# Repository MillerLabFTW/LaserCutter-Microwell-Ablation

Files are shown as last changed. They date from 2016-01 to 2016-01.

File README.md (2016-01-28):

# Laser Cutter Setup for Ablation of Microwells in PDMS

See accompanying journal article for more information: 
DOI: 10.1039/C5RA26022A 

##### A modified laser cutter platform for ablating microwells into PDMS
##### Miller Lab: Physiological Systems Engineering and Advanced Materials
##### [millerlab.rice.edu] (http://millerlab.rice.edu)
&nbsp;

MillerLab logo

We have custom modified a commercial SeeMeCNC laser cutter to selectively ablate microwell structures in PDMS. Using the modified laser cutter and our python scripts, you can print hexagonally packed arrays of microwells.

### Documentation
This git repository includes:
- STL files for 3D printing custom parts for the laser cutter
- Current Marlin firmware (modified Marlin for laser cutters courtesy of Tim Schmidt, Lansing-Maker-Network)
- Python scripts for G-code creation
- Wiring Diagram for electronics configuation (based on RAMBo electronics)
- Instructions for operating the laser cutter
- Bill of Materials

### Acknowledgements

The initial influence for using a laser cutter to ablate conical microwells comes from Roger Kamm's group at MIT:

Tu, Ting-Yuan, et al. "Rapid prototyping of concave microwells for the formation of 3D multicellular cancer aggregates for drug screening." Advanced healthcare materials 3.4 (2014): 609-616.

Tim Schmidt from the Lansing Makers Network developed the custom Marlin firmware for controlling a laser cutter.

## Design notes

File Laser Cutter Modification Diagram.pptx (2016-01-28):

## Laser Cutter Modifications

By: Jacob Albritton

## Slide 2

Z-axis linear actuator

3D Printed Vacuum hose holder

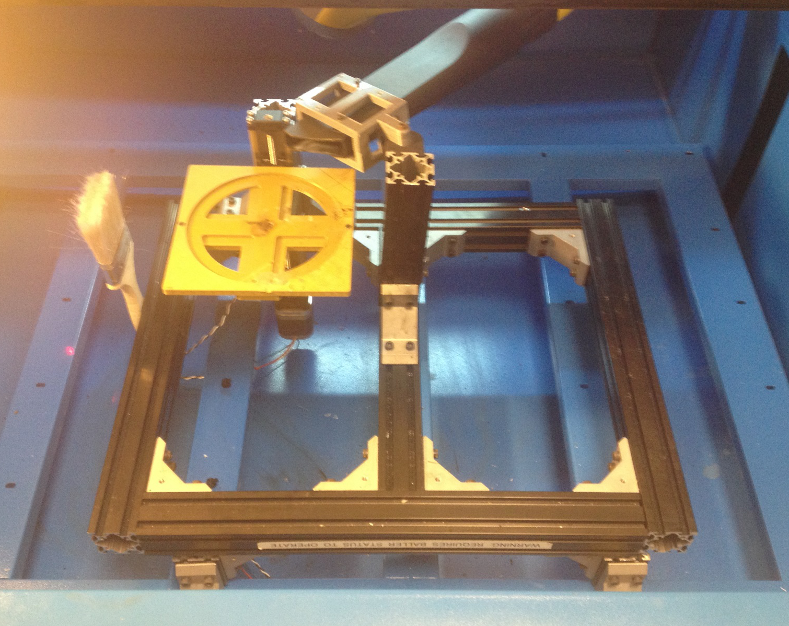
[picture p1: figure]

Laser Head Cleaning Brush

3D Printed platform

(Underneath the frame)

Z-axis motor

Frame Attachment to Laser Cutter

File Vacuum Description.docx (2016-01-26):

Updated Vacuum System

A vacuum holder has been added to the stage to secure the vacuum hose. The STL files for the vacuum hose holder parts can be found in the "STL for laser cutter" folder.

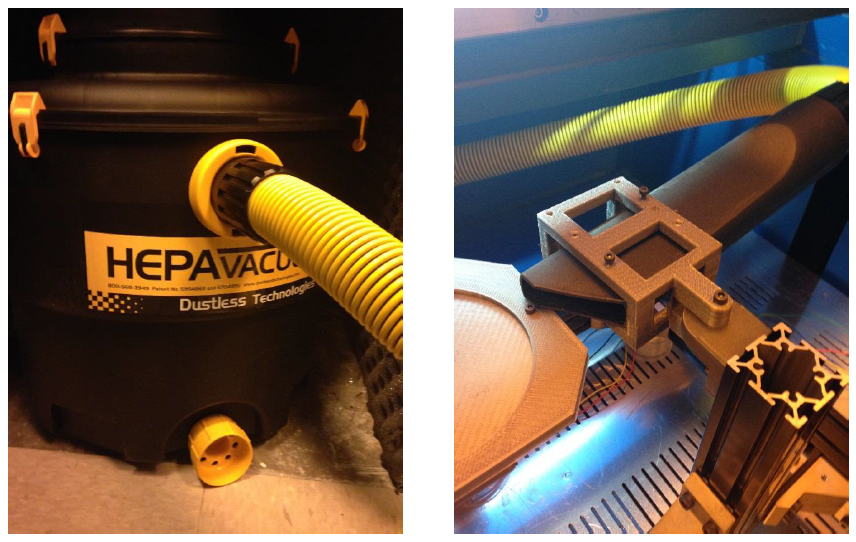
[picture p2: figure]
Machine generated alternative text: HEPAWC Dustkss т

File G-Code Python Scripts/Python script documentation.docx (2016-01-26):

Laser-ablation-GUI

This folder contains the major script for patterning rectangular arrays of microwells with the same laser parameters.

run.py

*****YOU MUST CHANGE THE FOCUS VARIABLE IN RUN.PY TO RUN PROPERLY. You can find the z-axis focus point by following the "focal point" protocol in the "Laser cutter operation" folder.

Tkinter GUI for making GCODE files for ablating PDMS with the laser cutter. The program displays a simple user interface with parameter boxes for all of the relevant parameters necessary to print.

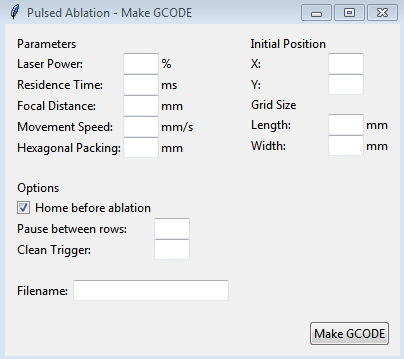
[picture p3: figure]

Pressing the Make GCODE button will create a file in a separate GCODE folder with a time and date stamp inside the filename.

NOTE: Must be run as using Python 3. Not compatible with Python 2.

Laser-ablation-functions

A few functions that can be used to create different patterns of microwells.

P-scan

Run script by running pscan.py. You can modify the config.py file to change the laser cutting parameters manually.

This program is a diagnostic tool for finding microwells of different dimensions. The program outputs a rough 3D matrix of microwell conditions based on inputs from "laserPowers", "dwellTimes" and "zValues".

The orientation parameter at the bottom will determine how the dimensions are displayed. See comments for details.

It is important to set the focus correctly. (See run.py description).

Circle-cut

Run script by running circle-cut.py. You can modify the config.py file to change the cut parameters.

Script to cut n-sided polygons with Laser Cutter toolchain. Parameters are currently optimized for cutting PDMS with our current z-axis system.

The current implementation (as of 5/2015) requires that the parameters be manually modified from the config.py file.

µWells-multishape

Run pulse.py.

Config.py file can be modified to change the parameters. Currently the simple script prints rows of alternative laser profile parameters. Each profile is the nth element of the array lists for laserPower, dwellTime, and zValue.

In theory, any number of laser profiles can be interleaved, but the program is not designed to account for printing too many shapes.

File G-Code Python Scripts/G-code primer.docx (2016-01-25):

GCODE Primer for Laser Cutter Control

General Information

Gcode is a very simple code designed to control 3D printers. We have an adapted version of a GCODE interpreter courtesy of Tim Schmidt from the Lansing Makers Network (https://github.com/lansing-makers-network/buildlog-lasercutter-marlin) that has been augmented to better control laser based machines like our laser cutter.

The flow of Gcode is fairly simple. Commands are given line by line with appropriate arguments. For example, a typical move command would look like this:

“G0 X1 Y2 Z3 F1000”

The initial command G0 specifies the function G0 to be applied. The following arguments are comprised of an initial letter to describe the type of argument, and a numerical value to quantify the argument. For example, the letters X, Y, and Z denote coordinates in the X, Y, and Z directions respectively. The numbers following X, Y, and Z show the coordinate value to move towards. The F value is a different argument, which specifies the movement speed. So 1000 quantifies how fast to move for this variable.

The Gcode RepRap wiki (http://reprap.org/wiki/G-code) gives a fairly comprehensive list of Gcode commands and appropriate descriptions. There are different Gcode interpreters including our interpreter (Marlin).

Interpreter firmware/Gcode syntax has been extensively used by the RepRap community to simplify the ability to control 3D printing movement. It is important to note though, that Gcode simply encodes for firing of electrical pulses in a predefined manner. So, even though Gcode was not designed for controlling a laser cutter, commands can be co-opted for unorthodox uses if the controller board is correctly wired to the laser cutter.

Below is a list of Gcode commands specific to our laser cutter/Marlin firmware setup with accompanying arguments and descriptions.

Important Commands for Controlling our Firmware

  - M649
    - Set Laser Fire Settings
    - Arguments
      - S
        - Laser Intensity
        - Values are 0 to 100 (float type)
        - Units are % laser power
      - L
        - Duration of laser pulse
        - Values are integers
        - Units are microseconds (μs)
      - P
        - Pulses per millimeter
        - Values are float type
        - Resolution discussed below
      - B
        - “Beam type”
        - 0 for continuous fire
        - 1 for Pulsed mode (note: specifying “P” should automatically change to B1 mode)
        - 2 for raster mode
      - D
        - Diagnostics
        - Logical 0 or 1 for whether to output diagnostics
  - M3
    - Turn laser on with current laser settings
    - Laser settings can be specified with an M3 command, but if a setting is not specified, the previously used value will be used.
  - M5
    - *****Turn laser off
  - G0
    - Move without laser on
    - Behaves identically with old marlin Gcode
  - G1
    - Move with laser on
    - Uses previously stored laser settings
    - Can take arguments from M649 to customize laser settings
  - M114
    - Obtain current coordinates
    - Enter directly to pronterface
    - Can be input while printing without disrupting the current print
  - G92
    - Set Coordinates
    - Takes X, Y, and Z arguments
  - G90
    - Set absolute coordinates
    - G0/G1 commands with X, Y, and Z will specify absolute coordinate locations
    - i.e. if you enter G0 X1 Y2 Z3 twice, the first command will move to (1,2,3) and the second command will not move (because you are already at the specified locations)
  - G91
    - Set relative coordinates
    - G0/G1 commands with X,Y, and Z will specify a relative movement direction
    - i.e. G0 X1 Y2 Z3 twice will move in a <1,2,3> vector direction twice to a final destination of (2, 4, 6) relative to the initial position
  - M84
    - Turn motors off

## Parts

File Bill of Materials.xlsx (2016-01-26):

Qty | Item | Vendor | Part No. | Cost Per Item | Total Cost | Notes
1 | CO2 Laser Cutter and Engraver With Auto Focus, Max 100W, RECI CO2 Glass Tube, Auto Focus, 48 ″ x 36″ - See more at: | Automation Technologies, Inc. |  | $8999.00 | $8999.00 | We use SeeMeCNC version that is no longer sold; this appears to be similar but may have different wiring
1 | RAMBo v1.3 Complete Kit w/ Mechanical Endstop Switches w/ Wiring | Ultimachine | UMRAMBOPAC13 | $170.00 | $170.00
1 | Kysan 1124090 Nema 17 Stepper Motor (z-motor) | Ultimachine | UMN17MTR | $14.50 | $14.50
1 | KR20 - 120mm stroke Linear motion actuator (z-axis) | THK |  | $200.00 | $200.00 | Actual price varies on Ebay
3 | Aluminum Frame | Misumi | HFSB5-4040-55 | $7.99 | $23.97
1 | Aluminum Frame | Misumi | HFSB5-4040-120 | $7.99 | $7.99
1 | Aluminum Frame | Misumi | HFSB5-4040-160 | $7.99 | $7.99
1 | Aluminum Frame | Misumi | HFSB5-4040-320 | $8.54 | $8.54
4 | Aluminum Frame | Misumi | HFSB5-4040-400 | $10.68 | $42.72
1 | Nuts for Aluminum Frames | Misumi | PACK-HNTT5-5 | $32.20 | $32.20
18 | Aluminum bracket | Misumi | HBLFUD5-C | $2.70 | $48.60
1 | paintbrush | various |  |  | $0.00
1 | Dustless Technologies 16006 16-Gallon Dustless Wet/Dry Vacuum with Hepa Filter | Amazon |  | $481.77 | $481.77
1 | Dustless Technologies 13141 Wet Dry Micro Pre Filter Bag, 2-Pack | Amazon |  | $19.95 | $19.95

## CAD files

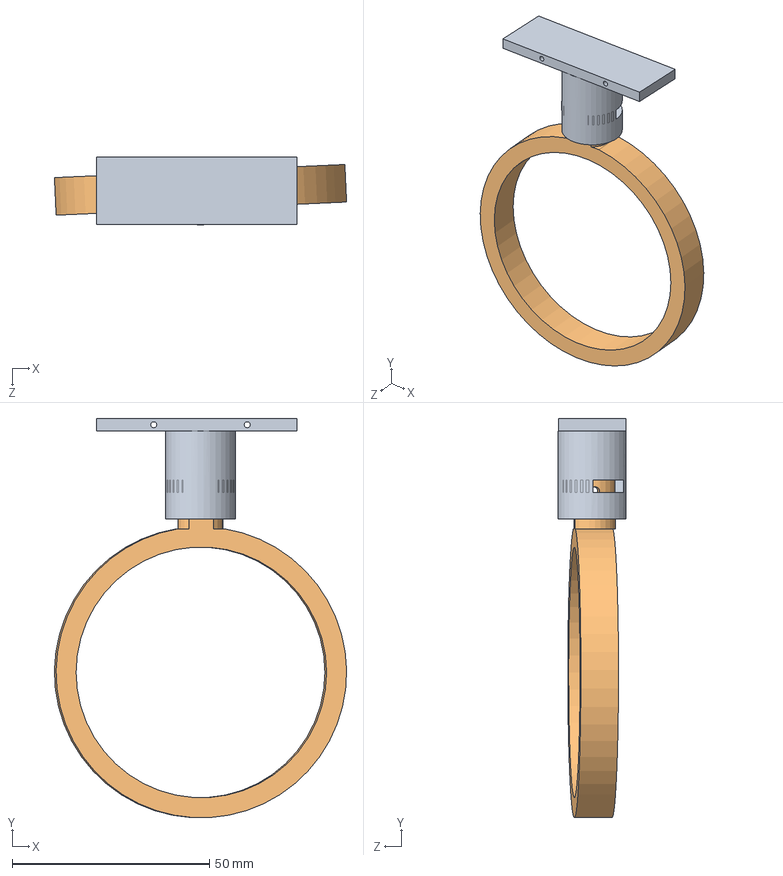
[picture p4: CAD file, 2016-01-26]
STL for laser cutter/VacuumHolder/VacuumFasten_002.SLDASM
74.0 x 101.1 x 17.1 mm
VacuumCuff
VacuumRing

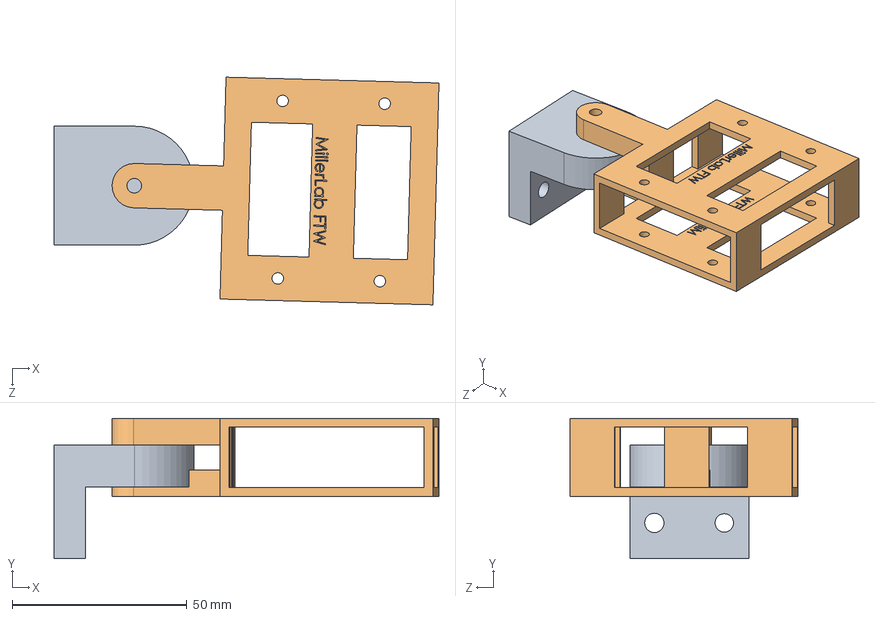
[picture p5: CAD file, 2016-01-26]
STL for laser cutter/VacuumHolder/VacuumFasten_001.SLDASM
110.2 x 40.1 x 65.1 mm
VacuumHinge
VacuumHolder

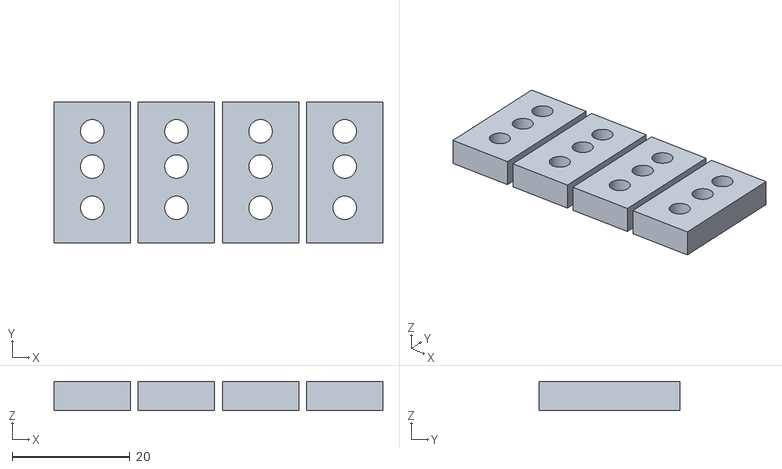
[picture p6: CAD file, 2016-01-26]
STL for laser cutter/Endstop holders/LaserCutter-Y-EndstopHolder.stl
55.9 x 24.0 x 5.00

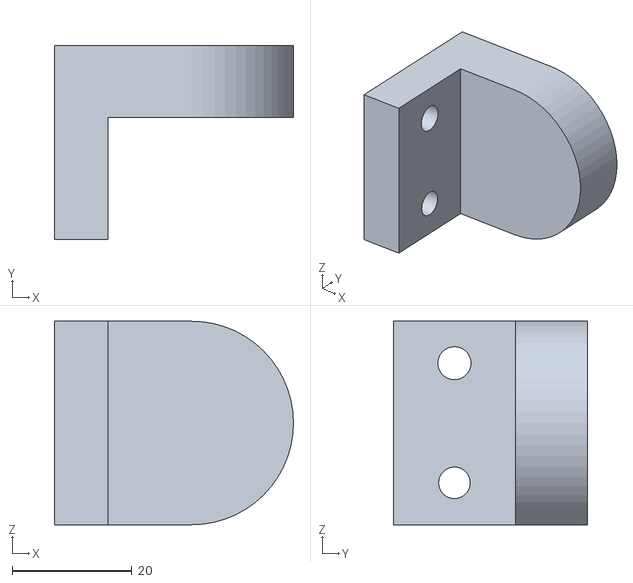
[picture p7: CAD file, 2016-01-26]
STL for laser cutter/Z-axis stage/VacuumHinge.STL
40.0 x 32.5 x 34.1

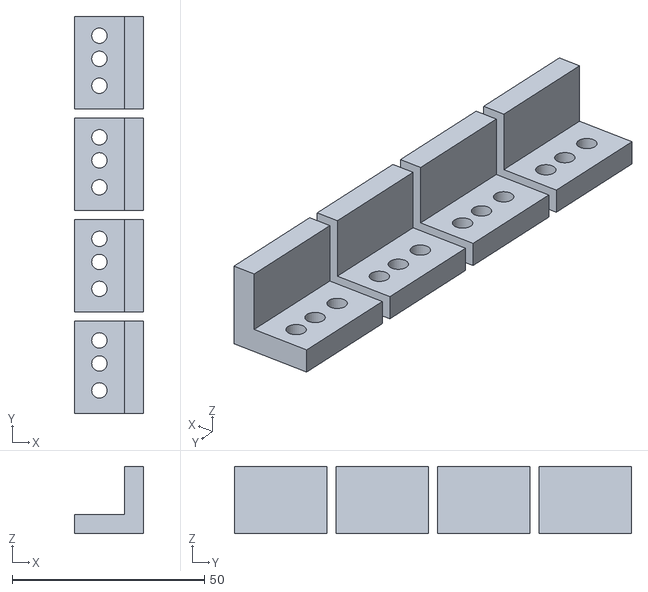
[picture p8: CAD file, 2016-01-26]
STL for laser cutter/Endstop holders/LaserCutter-X-EndstopHolder.stl
18.0 x 103.2 x 17.5

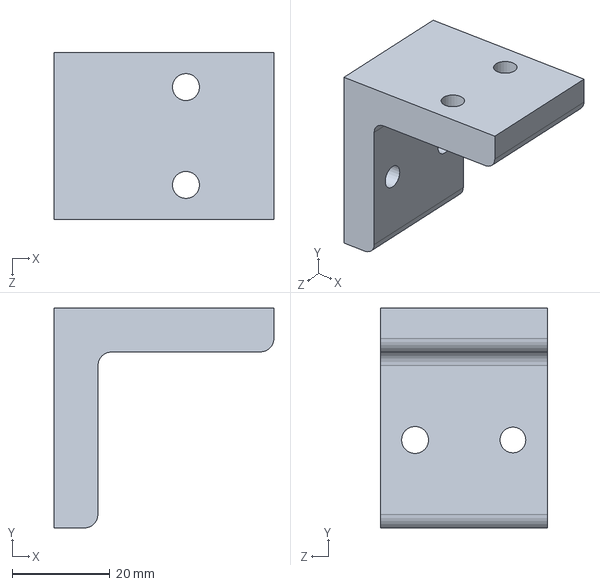
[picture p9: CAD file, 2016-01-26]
STL for laser cutter/Z-axis stage/80-20Bracket.SLDPRT
45.0 x 45.0 x 34.1 mm

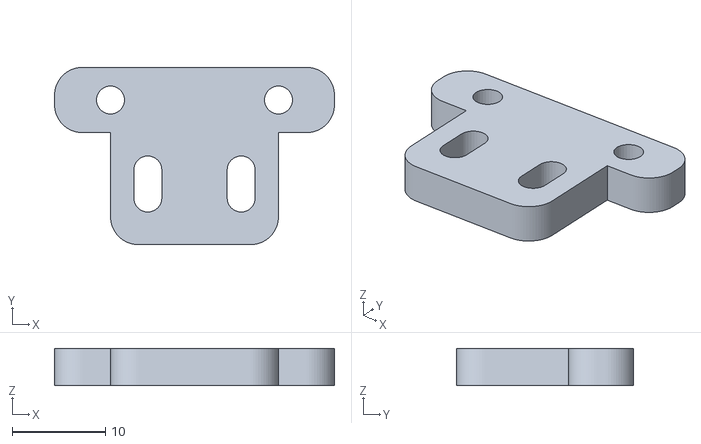
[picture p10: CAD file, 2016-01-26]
STL for laser cutter/Endstop holders/LaserCutter-Z-EndstopHolder.stl
30.0 x 19.0 x 4.00

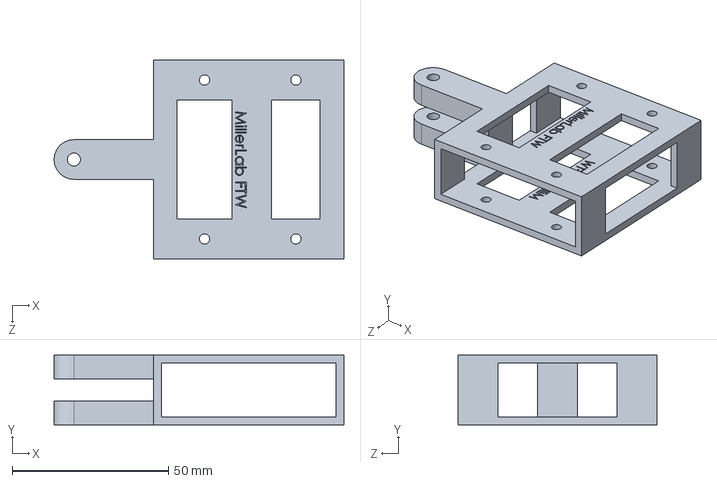
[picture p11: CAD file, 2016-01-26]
STL for laser cutter/VacuumHolder/VacuumHolder.SLDPRT
92.7 x 22.4 x 63.5 mm

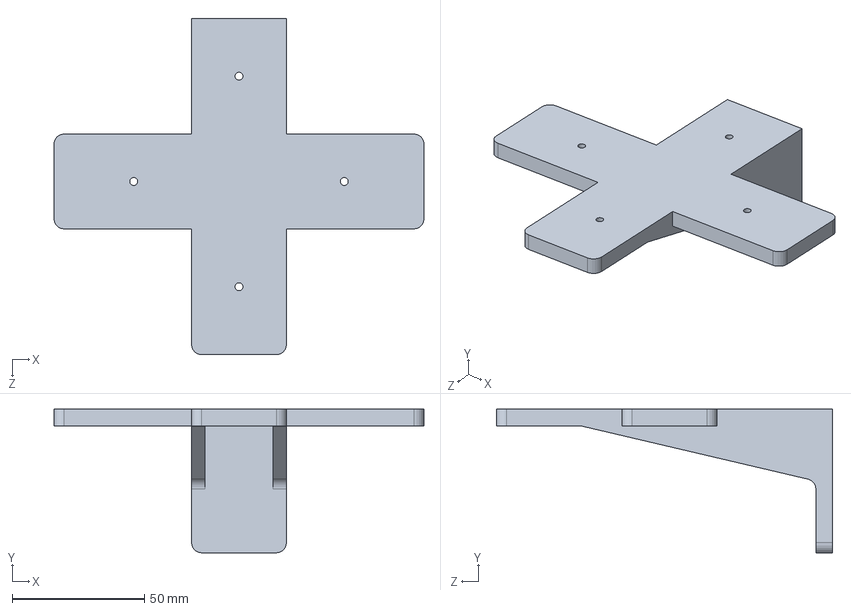
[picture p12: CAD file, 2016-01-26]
STL for laser cutter/Z-axis stage/Z-Stage_002.SLDPRT
139.7 x 54.2 x 127.0 mm

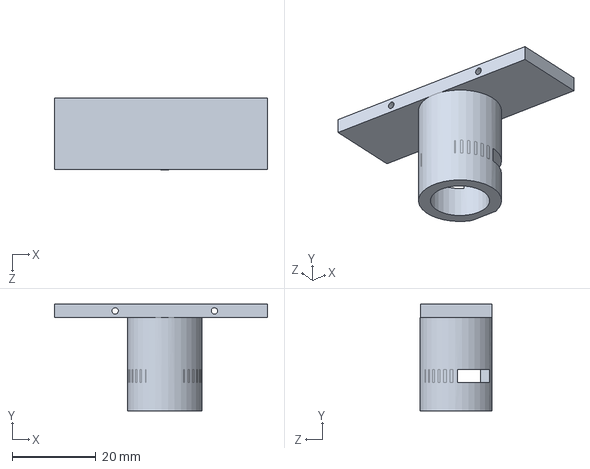
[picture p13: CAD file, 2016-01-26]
STL for laser cutter/VacuumHolder/VacuumCuff.SLDPRT
50.8 x 25.4 x 17.1 mm

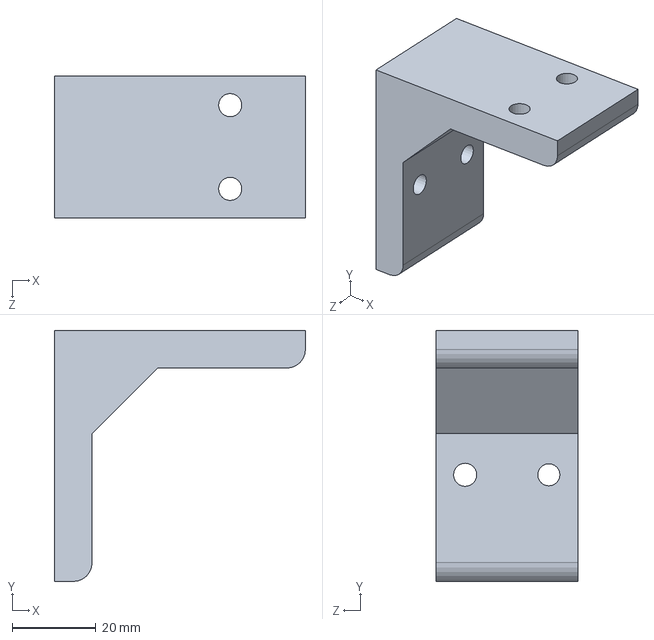
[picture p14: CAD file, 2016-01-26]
STL for laser cutter/Z-axis stage/PlatformFoot.SLDPRT
60.0 x 60.0 x 34.1 mm

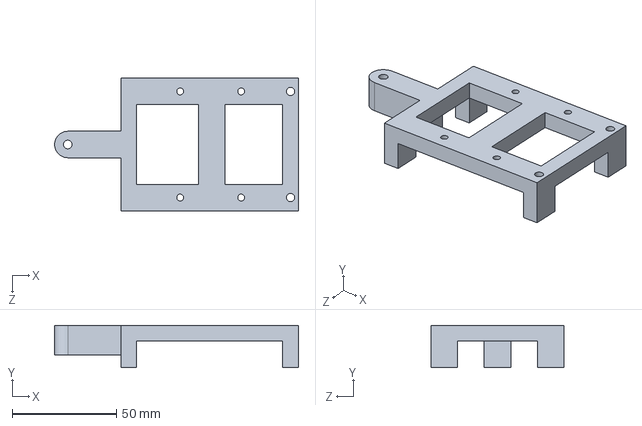
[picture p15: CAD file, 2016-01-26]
STL for laser cutter/VacuumHolder/VacuumHolder0.5.SLDPRT
116.8 x 20.3 x 63.5 mm

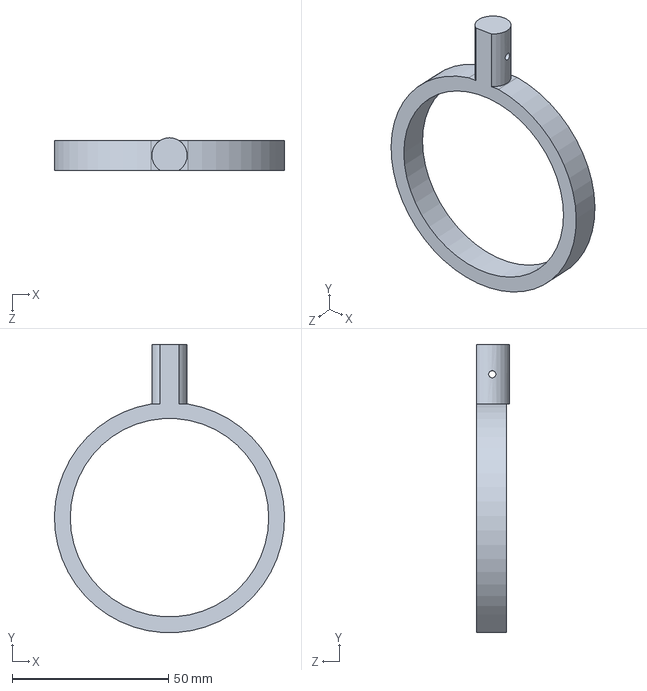
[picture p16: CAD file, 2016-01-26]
STL for laser cutter/VacuumHolder/VacuumRing.SLDPRT
73.7 x 92.2 x 10.4 mm

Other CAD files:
STL for laser cutter/VacuumHolder/VacuumHinge.SLDPRT
STL for laser cutter/Z-axis stage/PlatformFoot.STL

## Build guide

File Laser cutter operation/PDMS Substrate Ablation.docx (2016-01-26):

PDMS Substrate Ablation

Miller Lab

Jacob Albritton

Equipment/Materials

Procedure

1. Turn on the laser water pump. (Very important!)

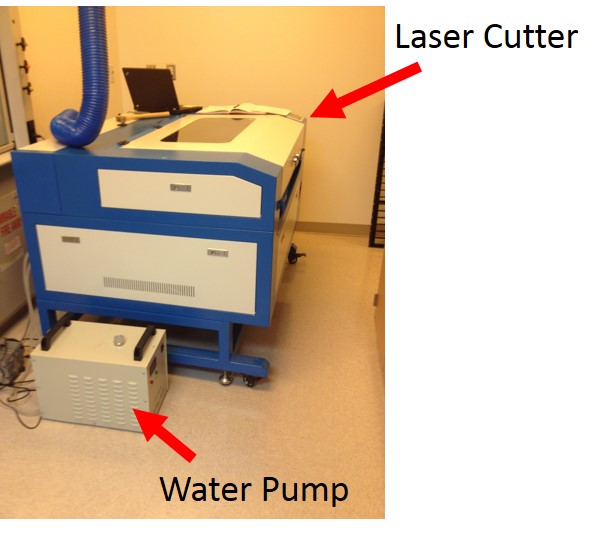
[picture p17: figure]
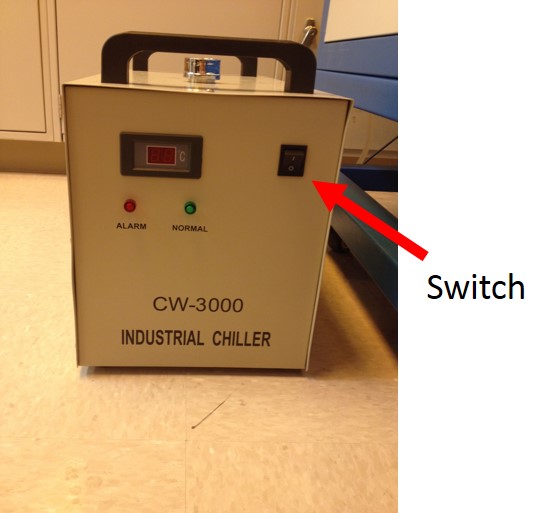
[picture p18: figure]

2. Verify that the laser water pump is running! The laser can overheat without cooling.

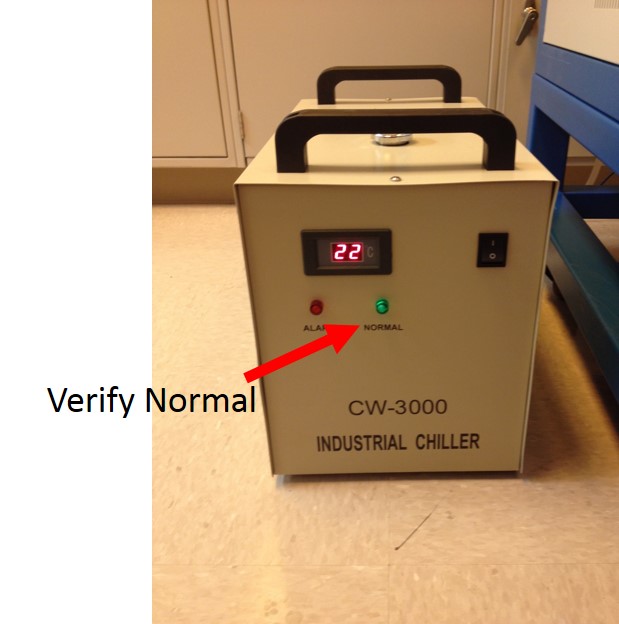
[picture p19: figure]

3. Verify that you verified that the laser water pump is on. (3 times)

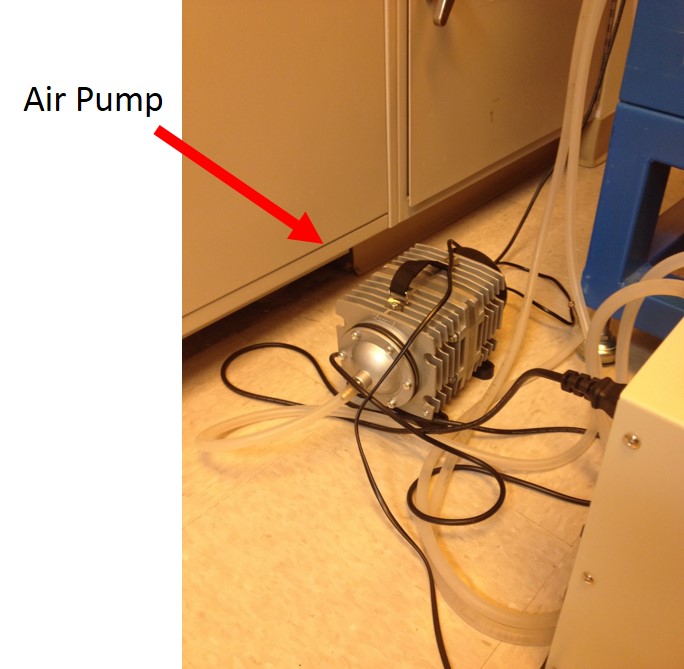
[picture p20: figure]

4. Turn on water pump, then the laser control unit (not the laser). To switch an emergency stop button on, twist the button clockwise about a quarter turn until the whole button releases outward. The RAMBo board will turn on with the laser control unit.

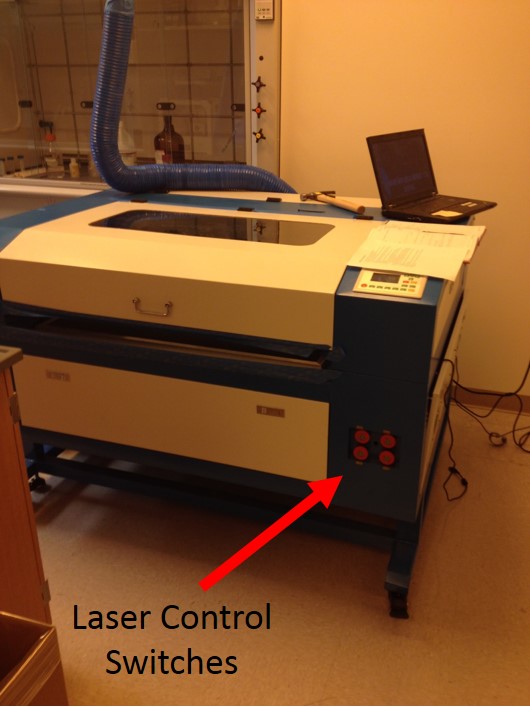
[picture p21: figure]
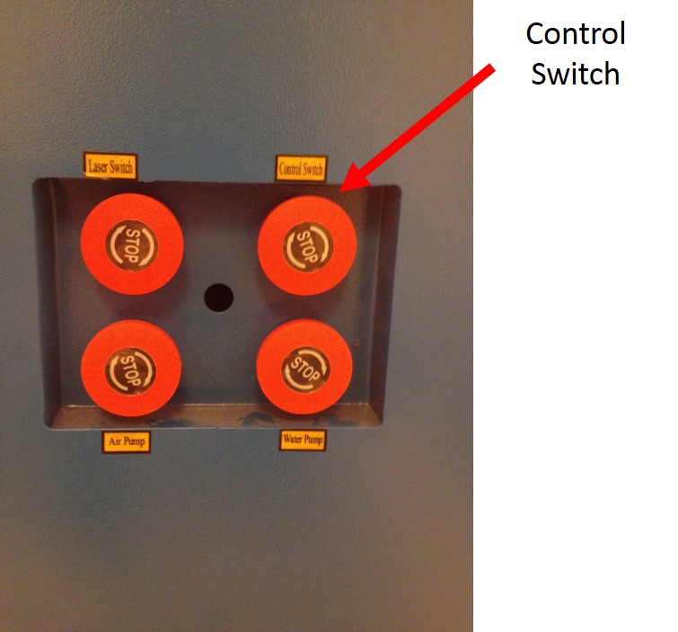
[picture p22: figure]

5. Plug the RAMBo USB cable to a Pronterface enabled computer.

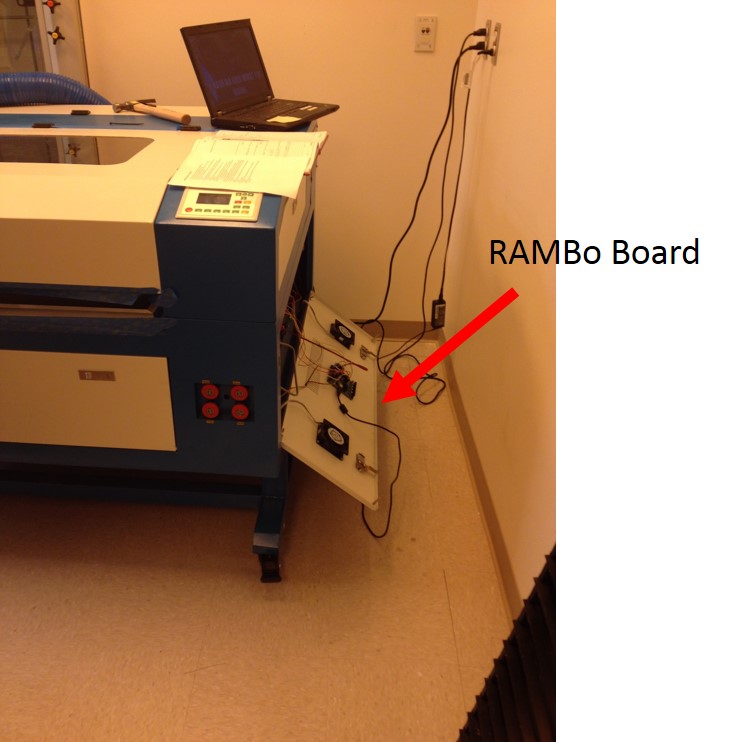
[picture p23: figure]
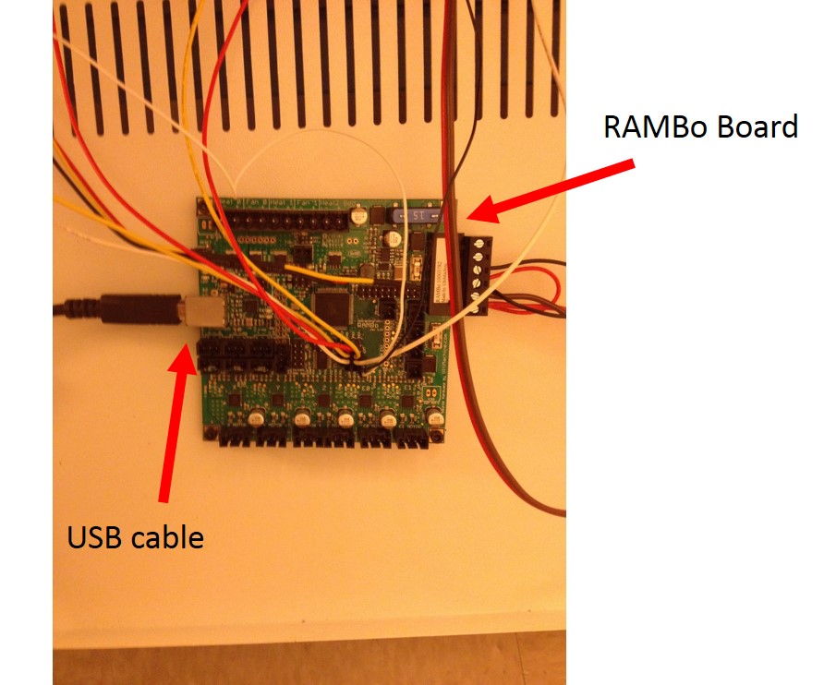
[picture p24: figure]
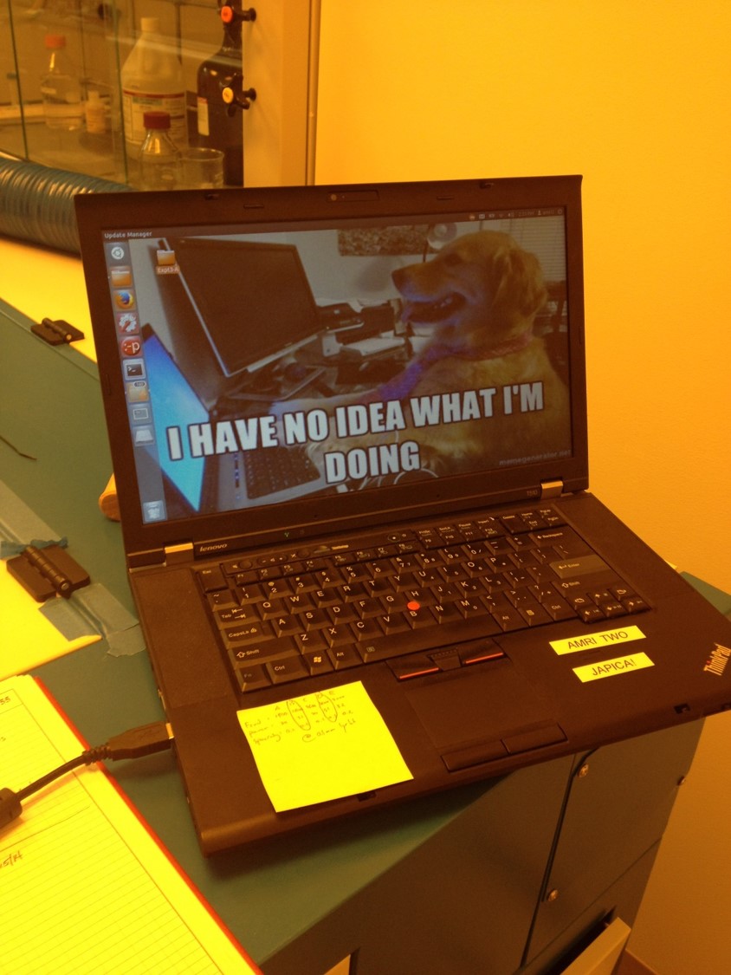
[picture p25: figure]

6. Start pronterface. After opening the terminal, navigate to the folder containing pronterface.py using the “cd” command. Use the “python” command with “pronterface.py” to open pronterface. Currently on the AMRI-Two lab computer, after opening the terminal, the following command should open pronterface:
  - python sls/Printrun/pronterface.py

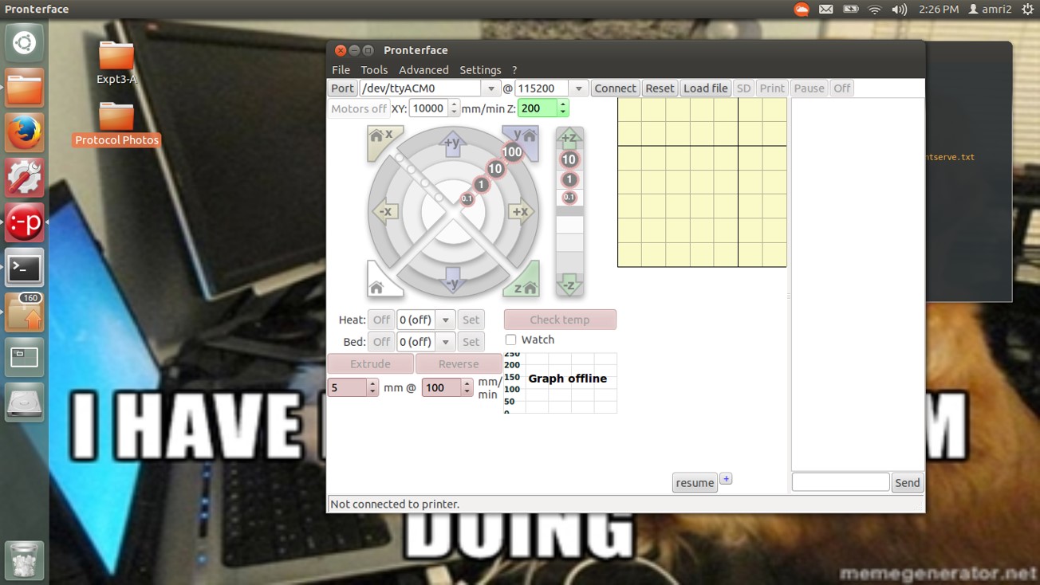
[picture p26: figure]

7. On pronterface, click on Connect to get the RAMBo board online. Make sure the Baudrate is set at 115200 (top dropdown box next to “@” symbol). You may also have to check different Com ports to get the right USB port.

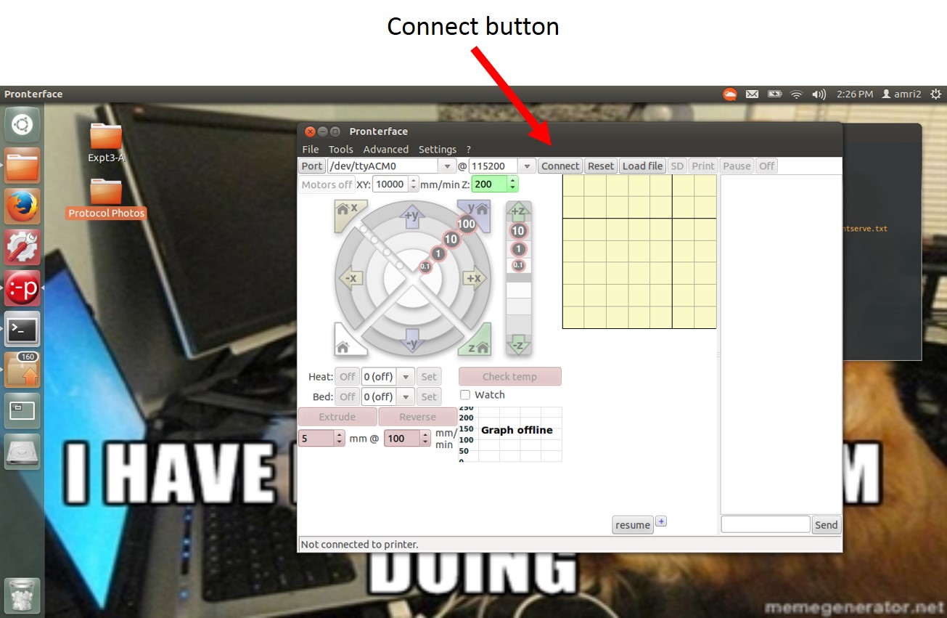
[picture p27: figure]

8. Test the connection by clicking on the home all button on Pronterface (bottom left button with house symbol). The laser head should move to the endstops in response.
9. Click on Load, and navigate to the .gcode file you have generated.
10. Manually move the laser head to the desired starting position using pronterface arrows labeled “+x”, “-x”, “+y”, and “-y”.

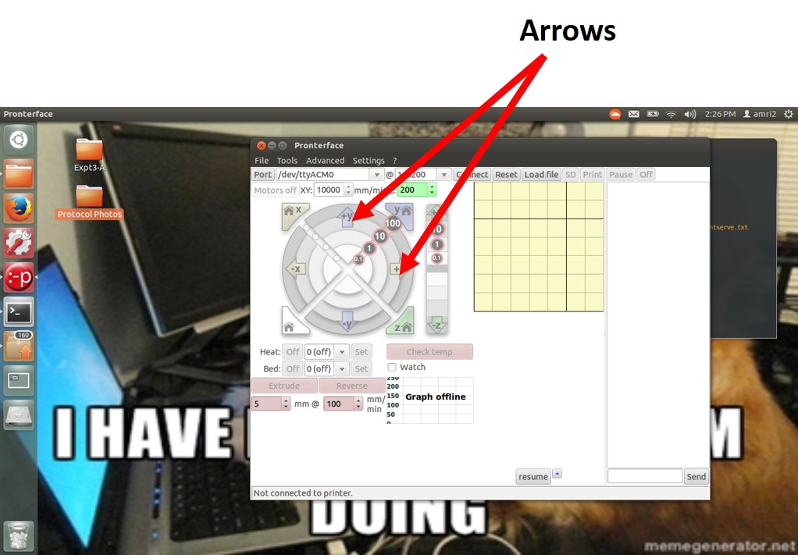
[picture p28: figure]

11. Turn on the laser.

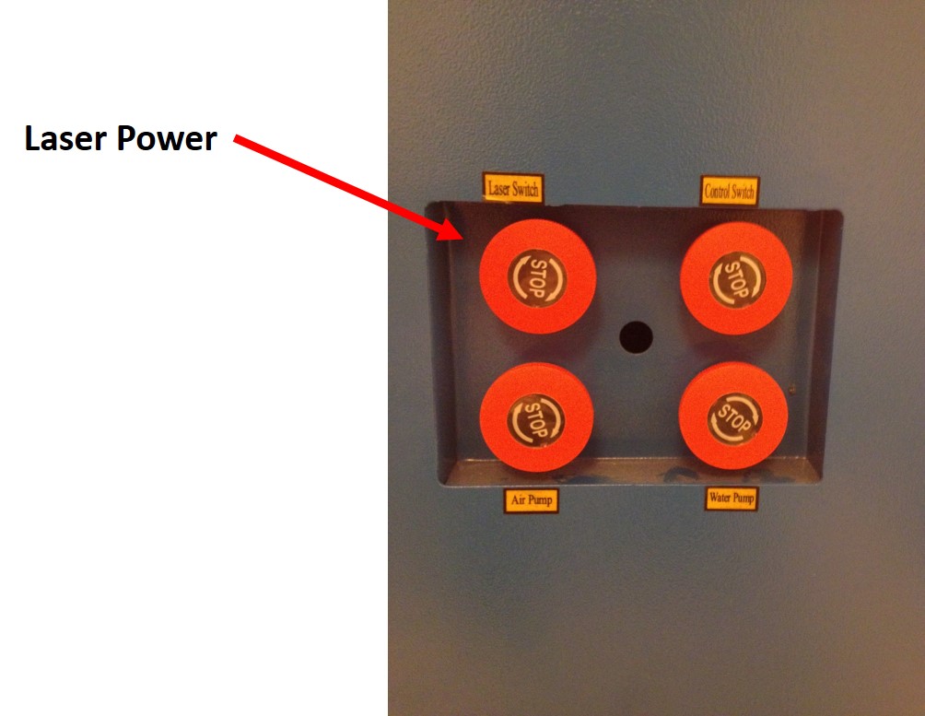
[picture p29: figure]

12. On pronterface, click print and wait until the laser starts ablating your sample.
13. Once the print is done turn off the machine in the following order
  - Laser Power
  - Laser Cutter Control
  - Air Pump/Water Pump
14. Turn water pump and unplug the air pump.

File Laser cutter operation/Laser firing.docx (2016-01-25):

Laser Cutter Firing Mechanism (Laser Power)

PWM/Laser Firing Profile

Laser Intensity is determined by pulse width modulation (PWM) of signals sent from the Arduino controller to the laser. The Arduino can send two voltage intensities to the laser cutter through the RAMBo microcontroller: a high and a low voltage. To modulate laser intensity with higher precision than on or off, the Arduino can send modulated square waves with controlled relative proportions of high vs. low signal that are integrated into an analog signal of approx. constant voltage by a capacitor (See PWM figure below).

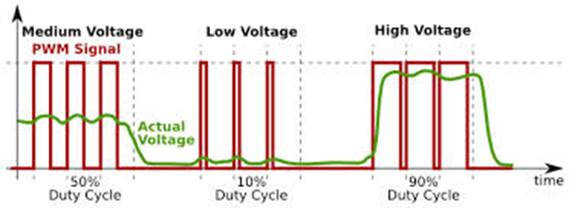
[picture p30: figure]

http://www.wayneandlayne.com/projects/video-game-shield/design/

Essentially, the laser accepts signals at a frequency determined by the internal capacitor. During each cycle, there are subcycles during which the signal can be a high or low voltage. The new firmware by Tim attempts to maximize control over laser intensity signaling by computing the smallest subcycle possible as determined from the physical capacitor and the Arduino processing power. Our laser cutter was similar to Tim’s laser cutter, so we estimated the capacitor frequency to be 25kHz. The Arduino has 16 MHz computing speed, so the number of subcycles possible are 16MHz / 25kHz = 640. By dividing the power range (0 to 100%) by 640, we calculate the approximate resolution of the power setting to be about 0.15625. Tim suggested that the resolution is probably about 0.2.

Laser settings can be changed in the Laser.cpp file (Ex. Capacitor frequency and Arduino Computing speed)

Beam Types

There are three potential beam types in the current marlin configuration: Continuous, Pulsed, and Raster.

  1. The continuous mode is the traditional laser cutting mode; i.e. during a movement, the laser is continuously open.
  2. The pulsed mode only fires the laser a set number of pulses per millimeter of movement,
    a. At low enough speeds (still relatively faster than previous ablation speeds), there is very nice ablation of the surface.
    b. This mode was determined to be extremely useful for my project.
  1. The raster code is not fully functional yet, and I don’t anticipate using that setting for my project, so I won’t discuss it here.

Signal firing characterization by oscilloscope observation

Background

We know nothing about the actual signals being conveyed from the RAMBo microcontroller to the laser cutter. Thus, I used an oscilloscope to generally observe output signals from the microcontroller in response to various basic GCODE commands.

  1. M3 [timed laser fire command] does not pause the command execution queue
    a. Movement commands will be executed immediately causing possible movement while laser is still firing

Solution: Insert a G4 [pause] command after every M3 command to force a pause in the GCODE for the M3 laser fire.

NOTE: G4 [pause] command cannot pause for less than 16 ms in actuality (even if less time is specified).

  2. If laser intensity is set, G0 movements become laser on movements (I have no idea why)

Solution: Manually set power to 0 by command “M3 S0 L10000”.

PWM Intensity Resolution

Background

It is also important to understand the resolution of the laser power intensity setting. From a signal standpoint, this means the smallest difference in input power settings that is distinguishable. To test this, I simply took measurements of the baseline PWM firing signal after changing the laser power. The microcontroller is constantly sending the intensity signal, so no code was needed to make measurements.

As a note, intensity can be effectively changed by issuing an M3 command like so:

"M3 Sx"

Where x denotes the Pulse Width Modulation ratio (PWM) in %.

System has integer value resolution of PWM settings with 0.1% accuracy

S1 is the lowest observable signal on the oscilloscope.

S1 input → 1.1% output

S2 input → 2.0% output

S1.5 input → 1.1% output

S12 input → 12% output

Further testing may yield different results, but tentatively, integer values of power input should safely give accuracy of +/- 0.1% power.

Power Resolution

Background

Laser signal PWM input does not necessarily correlate perfectly to max power. Here I measured the actual power output at different % power input settings to empirically determine actual power output. Unfortunately with a high powered laser, I cannot test the power at the focal region without potentially destroying the power meter. So, I placed the power meter on the laser cutter bed as far from the focal zone as possible to take power measurements.

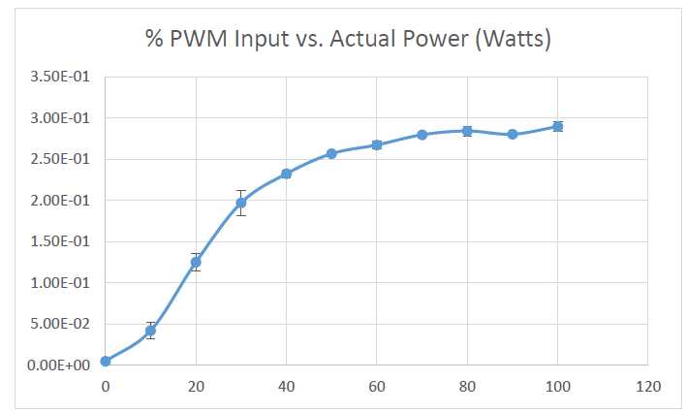
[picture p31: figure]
Machine generated alternative text: 0.00E + 00 5b0E102 1b0E101 1.50E101 2b0E101 2.50E101 3b0E101 3.50E101 0 PWM Inputvs.Actual Power(Watts) 100 120

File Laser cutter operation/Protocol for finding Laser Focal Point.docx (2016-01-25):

Protocol for finding Laser Focal Point

Equipment

- SeemeCNC Laser Cutter
- Z-axis Stage

Identify focal point by ablation diameter

1. Home the z-axis and raise the platform using pronterface or G0 commands to where the PDMS to be ablated is just below or touching the laser head. Be sure to have the PDMS in an experimental-like condition (with any extra material beneath it, etc. to simulate the actual distance to the PDMS surface). WARNING: When raising the platform, be careful near the laser head tip because collisions can damage the laser head.
2. Note the coordinates of the laser head from the home beacon using the M114 command in pronterface.
3. Find a power and dwell time for ablating PDMS that does not pierce the PDMS.
4. Successively ablate rows of microwells using the following command combinations:
  a. G92
  b. G0 Za
  c. G91
  d. G1 B1 P0.5 Sb Lc X10
  e. G0 X-10 Y3 Zd
  f. “Repeat c-d until well diameter begins to get bigger”
  g. Variable Explanation
    i. a -> Initial z-point that should be above the focal distance
    ii. b -> Power that does not pierce PDMS
    iii. c -> Dwell Time (μs) that does not pierce PDMS
    iv. d -> Resolution of z-focal distance desired; Should be negative number
      1. You can repeat this process successively with finer resolutions of z to get a better approximation of the focal distance.
1. The true focal distance will be the distance where the row of wells has the smallest diameter.
2. Once the focal distance from the laser head is identified, write down the number and use it for future experiments. If you’ve homed the z-axis correctly, then M114 should give the coordinates of the focal distance.

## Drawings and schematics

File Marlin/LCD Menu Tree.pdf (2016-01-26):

# Marlin LCD Menu Tree (V1)

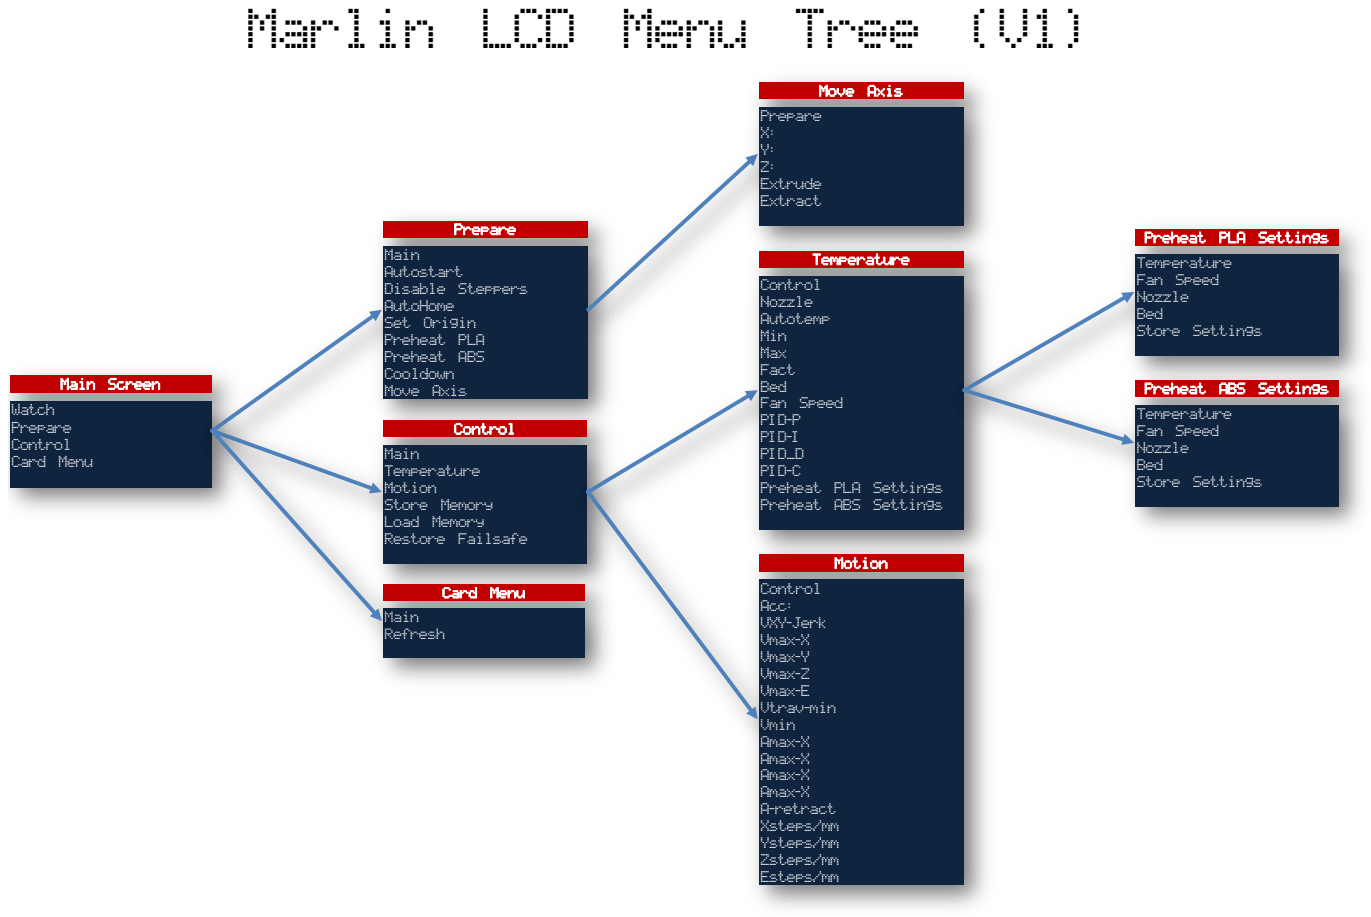
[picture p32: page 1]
Main Screen; Watch; Prepare; Control; Card Menu; Main; Autostart; Disable Steppers; AutoHome; Set Origin; Preheat PLA; Preheat ABS; Cooldown; Move Axis; Temperature; Motion; Store Memory; Load Memory; Restore Failsafe; Card; Menu; Refresh; Move; Axis; Extrude; Extract; Nozzle; Autotemp; Min; Max; Fact; Bed; Fan Speed; PID-P; PID-I; PID_D; PID-C; Preheat PLA Settings; Preheat ABS Settings; Acc:; VXY-Jerk; Vmax-X; Vmax-Y; Vmax-Z; Vmax-E; Vtrav-min; Vmin; Amax-X; A-retract; Xsteps/mm; Ysteps/mm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

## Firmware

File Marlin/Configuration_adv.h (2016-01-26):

#ifndef CONFIGURATION_ADV_H
#define CONFIGURATION_ADV_H

//===========================================================================
//=============================Thermal Settings  ============================
//===========================================================================

#ifdef BED_LIMIT_SWITCHING
  #define BED_HYSTERESIS 2 //only disable heating if T>target+BED_HYSTERESIS and enable heating if T>target-BED_HYSTERESIS
#endif
#define BED_CHECK_INTERVAL 5000 //ms between checks in bang-bang control

//// Heating sanity check:
// This waits for the watchperiod in milliseconds whenever an M104 or M109 increases the target temperature
// If the temperature has not increased at the end of that period, the target temperature is set to zero. 
// It can be reset with another M104/M109. This check is also only triggered if the target temperature and the current temperature
//  differ by at least 2x WATCH_TEMP_INCREASE
//#define WATCH_TEMP_PERIOD 40000 //40 seconds
//#define WATCH_TEMP_INCREASE 10  //Heat up at least 10 degree in 20 seconds

#ifdef PIDTEMP
  // this adds an experimental additional term to the heatingpower, proportional to the extrusion speed.
  // if Kc is choosen well, the additional required power due to increased melting should be compensated.
  #define PID_ADD_EXTRUSION_RATE  
  #ifdef PID_ADD_EXTRUSION_RATE
    #define  DEFAULT_Kc (1) //heatingpower=Kc*(e_speed)
  #endif
#endif


//automatic temperature: The hot end target temperature is calculated by all the buffered lines of gcode.
//The maximum buffered steps/sec of the extruder motor are called "se".
//You enter the autotemp mode by a M109 S<mintemp> T<maxtemp> F<factor>
// the target temperature is set to mintemp+factor*se[steps/sec] and limited by mintemp and maxtemp
// you exit the value by any M109 without F*
// Also, if the temperature is set to a value <mintemp, it is not changed by autotemp.
// on an ultimaker, some initial testing worked with M109 S215 B260 F1 in the start.gcode
#define AUTOTEMP
#ifdef AUTOTEMP
  #define AUTOTEMP_OLDWEIGHT 0.98
#endif

//  extruder run-out prevention. 
//if the machine is idle, and the temperature over MINTEMP, every couple of SECONDS some filament is extruded
//#define EXTRUDER_RUNOUT_PREVENT  
#define EXTRUDER_RUNOUT_MINTEMP 190  
#define EXTRUDER_RUNOUT_SECONDS 30.
#define EXTRUDER_RUNOUT_ESTEPS 14. //mm filament
#define EXTRUDER_RUNOUT_SPEED 1500.  //extrusion speed
#define EXTRUDER_RUNOUT_EXTRUDE 100

//These defines help to calibrate the AD595 sensor in case you get wrong temperature measurements.
//The measured temperature is defined as "actualTemp = (measuredTemp * TEMP_SENSOR_AD595_GAIN) + TEMP_SENSOR_AD595_OFFSET"
#define TEMP_SENSOR_AD595_OFFSET 0.0
#define TEMP_SENSOR_AD595_GAIN   1.0

//This is for controlling a fan to cool down the stepper drivers
//it will turn on when any driver is enabled
//and turn off after the set amount of seconds from last driver being disabled again
#define CONTROLLERFAN_PIN -1 //Pin used for the fan to cool controller (-1 to disable)
#define CONTROLLERFAN_SECS 60 //How many seconds, after all motors were disabled, the fan should run
#define CONTROLLERFAN_SPEED 255  // == full speed

// When first starting the main fan, run it at full speed for the
// given number of milliseconds.  This gets the fan spinning reliably
// before setting a PWM value. (Does not work with software PWM for fan on Sanguinololu)
//#define FAN_KICKSTART_TIME 100

// Extruder cooling fans
// Configure fan pin outputs to automatically turn on/off when the associated
// extruder temperature is above/below EXTRUDER_AUTO_FAN_TEMPERATURE.
// Multiple extruders can be assigned to the same pin in which case 
// the fan will turn on when any selected extruder is above the threshold.
#define EXTRUDER_0_AUTO_FAN_PIN   -1
#define EXTRUDER_1_AUTO_FAN_PIN   -1
#define EXTRUDER_2_AUTO_FAN_PIN   -1
#define EXTRUDER_AUTO_FAN_TEMPERATURE 50
#define EXTRUDER_AUTO_FAN_SPEED   255  // == full speed


//===========================================================================
//=============================Mechanical Settings===========================
//===========================================================================

//#define ENDSTOPS_ONLY_FOR_HOMING // If defined the endstops will only be used for homing


//// AUTOSET LOCATIONS OF LIMIT SWITCHES
//// Added by ZetaPhoenix 09-15-2012
#ifdef MANUAL_HOME_POSITIONS  // Use manual limit switch locations
  #define X_HOME_POS MANUAL_X_HOME_POS
  #define Y_HOME_POS MANUAL_Y_HOME_POS
  #define Z_HOME_POS MANUAL_Z_HOME_POS
#else //Set min/max homing switch positions based upon homing direction and min/max travel limits
  //X axis
  #if X_HOME_DIR == -1
    #ifdef BED_CENTER_AT_0_0
      #define X_HOME_POS X_MAX_LENGTH * -0.5
    #else
      #define X_HOME_POS X_MIN_POS
    #endif //BED_CENTER_AT_0_0
  #else    
    #ifdef BED_CENTER_AT_0_0
      #define X_HOME_POS X_MAX_LENGTH * 0.5
    #else
      #define X_HOME_POS X_MAX_POS
    #endif //BED_CENTER_AT_0_0
  #endif //X_HOME_DIR == -1
  
  //Y axis
  #if Y_HOME_DIR == -1
    #ifdef BED_CENTER_AT_0_0
      #define Y_HOME_POS Y_MAX_LENGTH * -0.5
    #else
      #define Y_HOME_POS Y_MIN_POS
    #endif //BED_CENTER_AT_0_0
  #else    
    #ifdef BED_CENTER_AT_0_0
      #define Y_HOME_POS Y_MAX_LENGTH * 0.5
    #else
      #define Y_HOME_POS Y_MAX_POS
    #endif //BED_CENTER_AT_0_0
  #endif //Y_HOME_DIR == -1
  
  // Z axis
  #if Z_HOME_DIR == -1 //BED_CENTER_AT_0_0 not used
    #define Z_HOME_POS Z_MIN_POS
  #else    
    #define Z_HOME_POS Z_MAX_POS
  #endif //Z_HOME_DIR == -1
#endif //End auto min/max positions
//END AUTOSET LOCATIONS OF LIMIT SWITCHES -ZP


//#define Z_LATE_ENABLE // Enable Z the last moment. Needed if your Z driver overheats.

// A single Z stepper driver is usually used to drive 2 stepper motors.
// Uncomment this define to utilize a separate stepper driver for each Z axis motor.
// Only a few motherboards support this, like RAMPS, which have dual extruder support (the 2nd, often unused, extruder driver is used
// to control the 2nd Z axis stepper motor). The pins are currently only defined for a RAMPS motherboards.
// On a RAMPS (or other 5 driver) motherboard, using this feature will limit you to using 1 extruder.
//#define Z_DUAL_STEPPER_DRIVERS

#ifdef Z_DUAL_STEPPER_DRIVERS
  #undef EXTRUDERS
  #define EXTRUDERS 1
#endif

// Enable this for dual x-carriage printers. 
// A dual x-carriage design has the advantage that the inactive extruder can be parked which
// prevents hot-end ooze contaminating the print. It also reduces the weight of each x-carriage
// allowing faster printing speeds.
//#define DUAL_X_CARRIAGE
#ifdef DUAL_X_CARRIAGE
// Configuration for second X-carriage
// Note: the first x-carriage is defined as the x-carriage which homes to the minimum endstop;
// the second x-carriage always homes to the maximum endstop.
#define X2_MIN_POS 80     // set minimum to ensure second x-carriage doesn't hit the parked first X-carriage
#define X2_MAX_POS 353    // set maximum to the distance between toolheads when both heads are homed 
#define X2_HOME_DIR 1     // the second X-carriage always homes to the maximum endstop position
#define X2_HOME_POS X2_MAX_POS // default home position is the maximum carriage position 
    // However: In this mode the EXTRUDER_OFFSET_X value for the second extruder provides a software 
    // override for X2_HOME_POS. This also allow recalibration of the distance between the two endstops
    // without modifying the firmware (through the "M218 T1 X???" command).
    // Remember: you should set the second extruder x-offset to 0 in your slicer.

// Pins for second x-carriage stepper driver (defined here to avoid further complicating pins.h)
#define X2_ENABLE_PIN 29
#define X2_STEP_PIN 25
#define X2_DIR_PIN 23

// There are a few selectable movement modes for dual x-carriages using M605 S<mode>
//    Mode 0: Full control. The slicer has full control over both x-carriages and can achieve optimal travel results
//                           as long as it supports dual x-carriages. (M605 S0)
//    Mode 1: Auto-park mode. The firmware will automatically park and unpark the x-carriages on tool changes so
//                           that additional slicer support is not required. (M605 S1)
//    Mode 2: Duplication mode. The firmware will transparently make the second x-carriage and extruder copy all  
//                           actions of the first x-carriage. This allows the printer to print 2 arbitrary items at
//                           once. (2nd extruder x offset and temp offset are set using: M605 S2 [Xnnn] [Rmmm])

// This is the default power-up mode which can be later using M605. 
#define DEFAULT_DUAL_X_CARRIAGE_MODE 0 

// As the x-carriages are independent we can now account for any relative Z offset
#define EXTRUDER1_Z_OFFSET 0.0           // z offset relative to extruder 0

// Default settings in "Auto-park Mode" 
#define TOOLCHANGE_PARK_ZLIFT   0.2      // the distance to raise Z axis when parking an extruder
#define TOOLCHANGE_UNPARK_ZLIFT 1        // the distance to raise Z axis when unparking an extruder

// Default x offset in duplication mode (typically set to half print bed width)
#define DEFAULT_DUPLICATION_X_OFFSET 100

#endif //DUAL_X_CARRIAGE
    
//homing hits the endstop, then retracts by this distance, before it tries to slowly bump again:
#define X_HOME_RETRACT_MM 5 
#define Y_HOME_RETRACT_MM 5 
#define Z_HOME_RETRACT_MM 1 
#define QUICK_HOME  //if this is defined, if both x and y are to be homed, a diagonal move will be performed initially.

#define AXIS_RELATIVE_MODES {false, false, false, false}

#define MAX_STEP_FREQUENCY 40000 // Max step frequency for Ultimaker (5000 pps / half step)

//By default pololu step drivers require an active high signal. However, some high power drivers require an active low signal as step.
#define INVERT_X_STEP_PIN false
#define INVERT_Y_STEP_PIN false
#define INVERT_Z_STEP_PIN false
#define INVERT_E_STEP_PIN false

//default stepper release if idle
// AMRI Laser cutter
#define DEFAULT_STEPPER_DEACTIVE_TIME 0

// LMN Laser cutter
//#define DEFAULT_STEPPER_DEACTIVE_TIME 60

#define DEFAULT_MINIMUMFEEDRATE       0.0     // minimum feedrate
#define DEFAULT_MINTRAVELFEEDRATE     0.0

// Feedrates for manual moves along X, Y, Z, E from panel
#ifdef ULTIPANEL
#define MANUAL_FEEDRATE {50*60, 50*60, 4*60, 60}  // set the speeds for manual moves (mm/min)
#endif

// minimum time in microseconds that a movement needs to take if the buffer is emptied.
#define DEFAULT_MINSEGMENTTIME        20000

// If defined the movements slow down when the look ahead buffer is only half full
#define SLOWDOWN

// Frequency limit
// See nophead's blog for more info
// Not working O
//#define XY_FREQUENCY_LIMIT  15

// Minimum planner junction speed. Sets the default minimum speed the planner plans for at the end
// of the buffer and all stops. This should not be much greater than zero and should only be changed
// if unwanted behavior is observed on a user's machine when running at very slow speeds.
#define MINIMUM_PLANNER_SPEED 0.05// (mm/sec)

// MS1 MS2 Stepper Driver Microstepping mode table
#define MICROSTEP1 LOW,LOW
#define MICROSTEP2 HIGH,LOW
#define MICROSTEP4 LOW,HIGH
#define MICROSTEP8 HIGH,HIGH
#define MICROSTEP16 HIGH,HIGH

// Microstep setting (Only functional when stepper driver microstep pins are connected to MCU.
#define MICROSTEP_MODES {16,16,16,16,16} // [1,2,4,8,16]

// Motor Current setting (Only functional when motor driver current ref pins are connected to a digital trimpot on supported boards)
#define DIGIPOT_MOTOR_CURRENT {135,135,135,135,135} // Values 0-255 (RAMBO 135 = ~0.75A, 185 = ~1A)


//===========================================================================
//=============================Additional Features===========================
//===========================================================================
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

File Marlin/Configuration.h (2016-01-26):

#ifndef CONFIGURATION_H
#define CONFIGURATION_H

// This configuration file contains the basic settings.
// Advanced settings can be found in Configuration_adv.h
// BASIC SETTINGS: select your board type, temperature sensor type, axis scaling, and endstop configuration

// User-specified version info of this build to display in [Pronterface, etc] terminal window during
// startup. Implementation of an idea by Prof Braino to inform user that any changes made to this
// build by the user have been successfully uploaded into firmware.
#define STRING_VERSION_CONFIG_H __DATE__ " " __TIME__ // build date and time
#define STRING_CONFIG_H_AUTHOR "(jmil, Jacob Ablative Laser, 2014-08-26)" // Who made the changes.

// SERIAL_PORT selects which serial port should be used for communication with the host.
// This allows the connection of wireless adapters (for instance) to non-default port pins.
// Serial port 0 is still used by the Arduino bootloader regardless of this setting.
#define SERIAL_PORT 0

// This determines the communication speed of the printer
//#define BAUDRATE 250000
#define BAUDRATE 115200

//// The following define selects which electronics board you have. Please choose the one that matches your setup
// 10 = Gen7 custom (Alfons3 Version) "https://github.com/Alfons3/Generation_7_Electronics"
// 11 = Gen7 v1.1, v1.2 = 11
// 12 = Gen7 v1.3
// 13 = Gen7 v1.4
// 3  = MEGA/RAMPS up to 1.2 = 3
// 33 = RAMPS 1.3 / 1.4 (Power outputs: Extruder, Fan, Bed)
// 34 = RAMPS 1.3 / 1.4 (Power outputs: Extruder0, Extruder1, Bed)
// 35 = RAMPS 1.3 / 1.4 (Power outputs: Extruder, Fan, Fan)
// 4  = Duemilanove w/ ATMega328P pin assignment
// 5  = Gen6
// 51 = Gen6 deluxe
// 6  = Sanguinololu < 1.2
// 62 = Sanguinololu 1.2 and above
// 63 = Melzi
// 64 = STB V1.1
// 65 = Azteeg X1
// 66 = Melzi with ATmega1284 (MaKr3d version)
// 7  = Ultimaker
// 71 = Ultimaker (Older electronics. Pre 1.5.4. This is rare)
// 77 = 3Drag Controller
// 8  = Teensylu
// 80 = Rumba
// 81 = Printrboard (AT90USB1286)
// 82 = Brainwave (AT90USB646)
// 9  = Gen3+
// 70 = Megatronics
// 701= Megatronics v2.0
// 702= Minitronics v1.0
// 90 = Alpha OMCA board
// 91 = Final OMCA board
// 301 = Rambo
// 21 = Elefu Ra Board (v3)

#ifndef MOTHERBOARD
#define MOTHERBOARD 301
#endif

// Define this to set a custom name for your generic Mendel,
// #define CUSTOM_MENDEL_NAME "This Mendel"

// This defines the number of extruders
#define EXTRUDERS 2

//// The following define selects which power supply you have. Please choose the one that matches your setup
// 1 = ATX
// 2 = X-Box 360 203Watts (the blue wire connected to PS_ON and the red wire to VCC)

#define POWER_SUPPLY 1

//===========================================================================
//============================= Laser Settings ==============================
//===========================================================================
//
// Laser control is used by the Muve1 3D printer and the Buildlog.net laser cutter
//
#define LASER
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

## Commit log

2016-01-25 added significant documentation and wiring diagram
2016-01-26 major additions: STL files, bill of materials, and laser cutter operation descriptions
    [80-20Bracket.SLDPRT, Bill of Materials.xlsx, LaserCutter-X-EndstopHolder.stl, LaserCutter-Y-EndstopHolder.stl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]
2016-01-26 major additions
    [LaserCutter-X-EndstopHolder.stl, LaserCutter-Y-EndstopHolder.stl, LaserCutter-Z-EndstopHolder.stl, LaserCutterEndstopHolder.blend]
2016-01-26 added marlin firmware; minor updates
    [Menu Plans.xlsx]
2016-01-28 added basic picture of laser cutter modifications
